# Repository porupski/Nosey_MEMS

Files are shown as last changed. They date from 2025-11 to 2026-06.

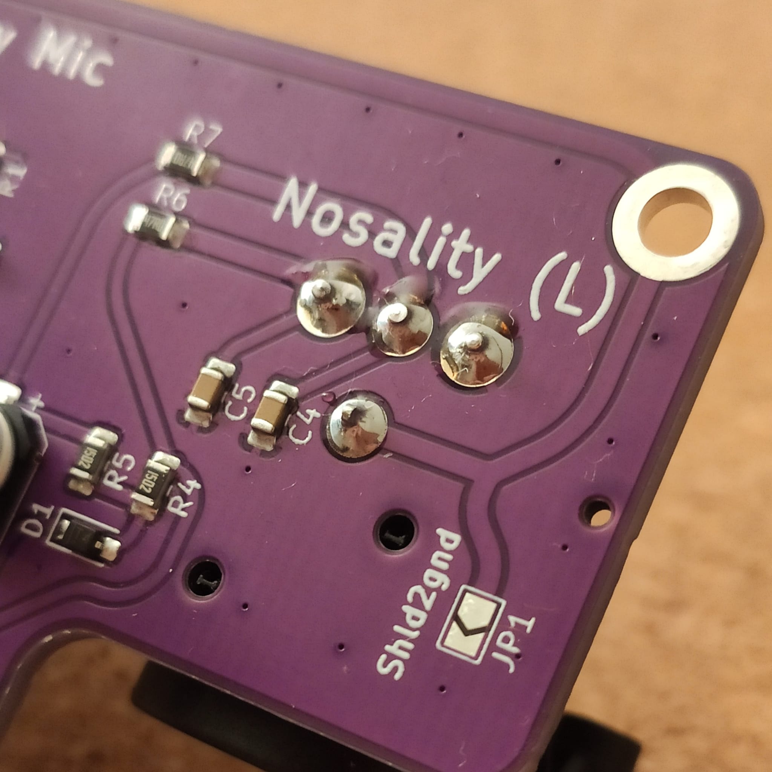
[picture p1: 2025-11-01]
docs/img/Nosey_MEMS_soldering_2.jpeg

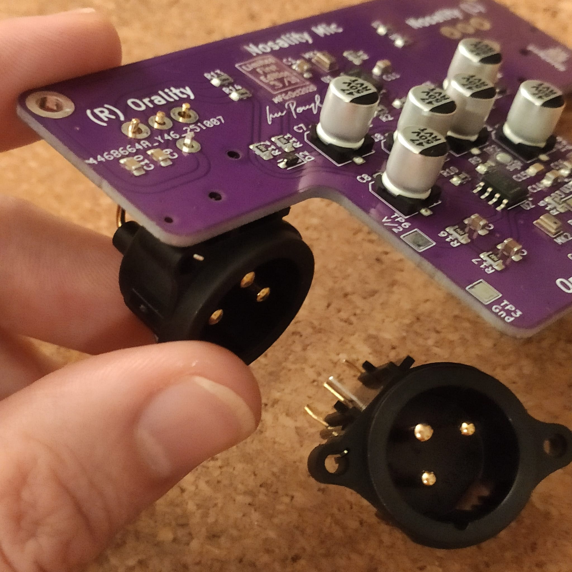
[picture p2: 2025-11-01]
docs/img/Nosey_MEMS_soldering_1.jpeg

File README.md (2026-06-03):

# Nosey MEMS

**/ˈnɔɪzi miːmz/** — a fully open-source nasometer.

Nosey MEMS is a general purpose **mono MEMS microphone preamp**. It was specifically designed for integration with **Nosey** ([GitHub](https://github.com/phoneticslab/nosey) [Paper, IS25](https://www.isca-archive.org/interspeech_2025/dewhurst25_interspeech.pdf)) for acoustic nasalance measurements. A **stereo pair of boards** — one nasal, one oral — in the (not yet) adapted Nosey 3D-printed handle and baffle.

## What you get

- Open **KiCad 10.0** schematic, PCB and JLCPCB production files
- Small 25 × 50 mm board: NA-FFA381-A10-1 MEMS mic, OPA1652 balanced output, +48V phantom via XLR3
- Simple, low-cost (~€20 per built board as of June 2026), low-maintenance design
- Built for general purpose, aimed at phonetics, but the schematic/PCB can be adapted to any use

## Where to look

- **Documentation:** [porupski.github.io/Nosey_MEMS](https://porupski.github.io/Nosey_MEMS/)
- **`KiCad_files/`** — schematic, PCB layout, production `.zip`
- **`REW_files/`** — measured frequency response (Mk1 measurements, but the circuity is basically identical)
- **`docs/legacy_mk1/`** — the first, stereo Mk1 design (superseded)

## Status

In active development. The mono Mk2 replaces the earlier single-board stereo prototype, whose shared layout compromised acoustic separation between the nasal and oral channels.

## References

- Dewhurst et al. (2025). *Nosey: Open-source hardware for acoustic nasalance.* [arXiv:2505.23339](https://arxiv.org/pdf/2505.23339) · [IS25 PDF](https://www.isca-archive.org/interspeech_2025/dewhurst25_interspeech.pdf)

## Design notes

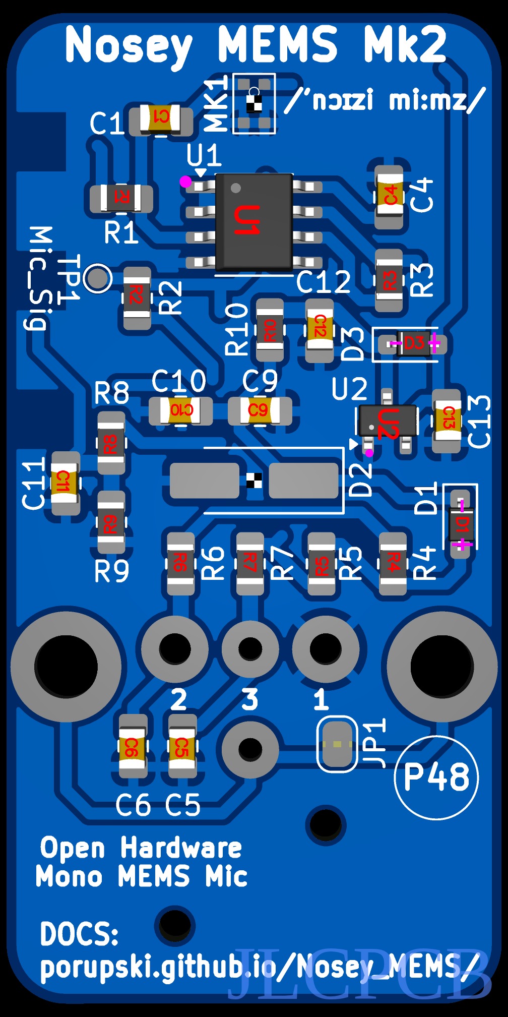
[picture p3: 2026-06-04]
docs/img/fab_Nosey_MEMS_Mk2_PCBA_placement_1.png

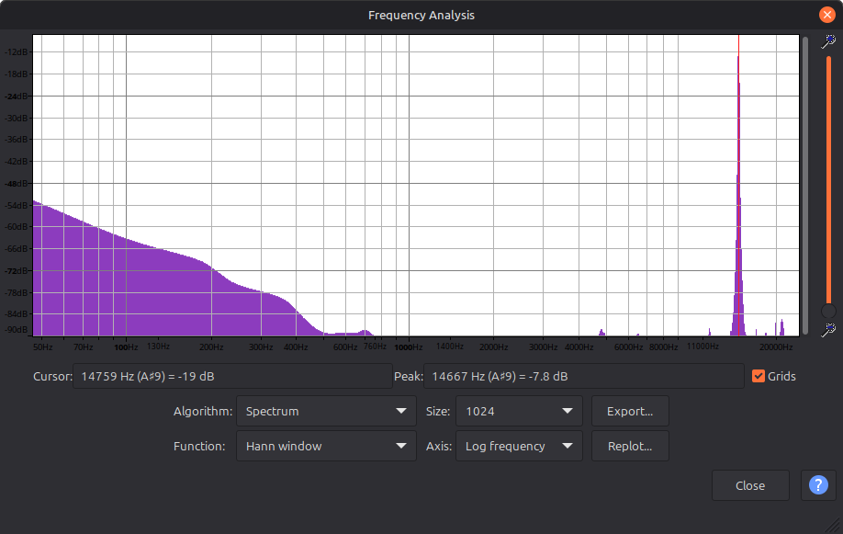
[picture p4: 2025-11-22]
docs/img/audio_plots/NoseyMEMS-R-self-resonance.png

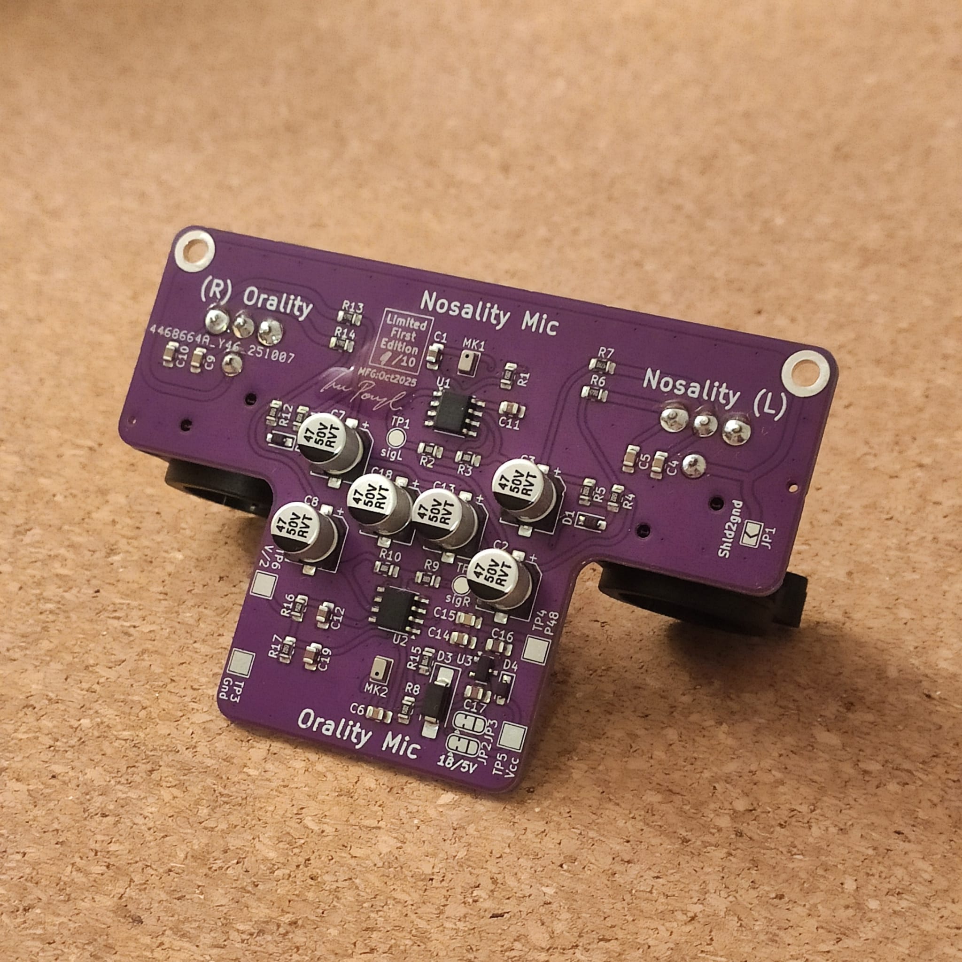
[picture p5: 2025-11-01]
docs/img/Nosey_MEMS_hero-shot_front.jpeg

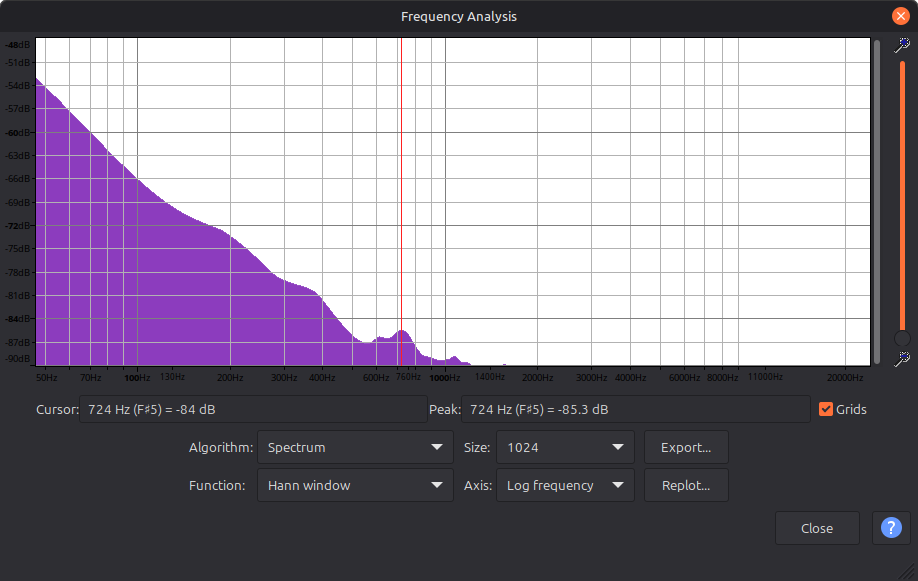
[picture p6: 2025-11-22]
docs/img/audio_plots/NoseyMEMS-R-noise.png

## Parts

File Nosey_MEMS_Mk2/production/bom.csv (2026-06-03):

Designator | Footprint | Quantity | Value | LCSC Part #
C1, C4, C9 | 0805 | 3 | 2.2uF
C10 | 0805 | 1 | 10nF
C11, C12, C13 | 0805 | 3 | 10uF
C2, C3, C7, C8 | CP_Elec_6.3x7.7 | 4 | 47uF
C5, C6 | 0805 | 2 | 22nF
D1, D3 | D_SOD-323_HandSoldering | 2 | 1N4148
D2 | D_SMA_Handsoldering | 1 | 1SMA4746A
MK1 | NA-FFA381-A10-1_MEMS_mic_analog_v1 | 1 | NA-FFA381-A10-1
R1, R4, R5, R8, R9 | 0805 | 5 | 15k
R10 | 0805 | 1 | 470R
R2, R3 | 0805 | 2 | 3k
R6, R7 | 0805 | 2 | 47R
U1 | SOIC-8_3.9x4.9mm_P1.27mm | 1 | OPA1652
U2 | SOT-23 | 1 | PJ71K30SC

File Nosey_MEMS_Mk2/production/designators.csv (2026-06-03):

C1:1
C10:1
C11:1
C12:1
C13:1
C2:1
C3:1
C4:1
C5:1
C6:1
C7:1
C8:1
C9:1
D1:1
D2:1
D3:1
H1:1
H2:1
J1:1
JP1:1
JP2:1
JP3:1
MK1:1
R1:1
R10:1
R2:1
R3:1
R4:1
R5:1
R6:1
R7:1
R8:1
R9:1
TP1:1
TP2:1
TP3:1
TP4:1
TP5:1
U1:1
U2:1

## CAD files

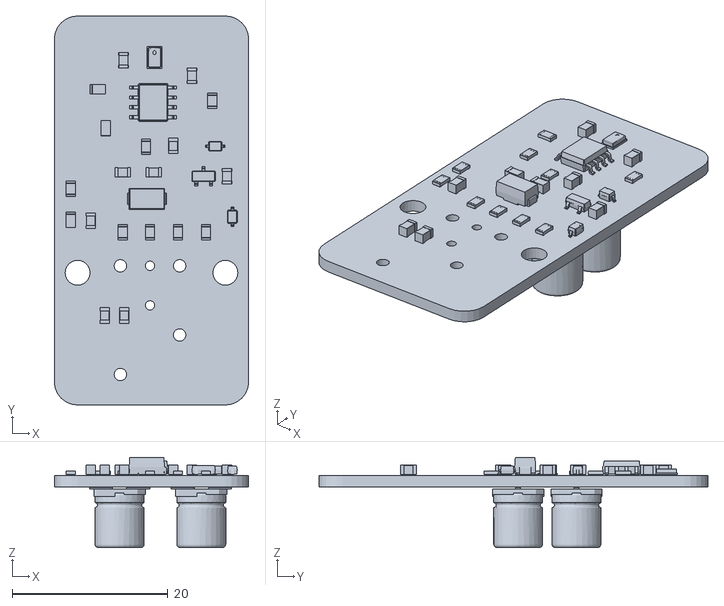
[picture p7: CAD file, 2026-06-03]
Nosey_MEMS_Mk2/Nosey_MEMS_Mk2_PCB_model_iv2.1.stl
25.0 x 50.0 x 11.6

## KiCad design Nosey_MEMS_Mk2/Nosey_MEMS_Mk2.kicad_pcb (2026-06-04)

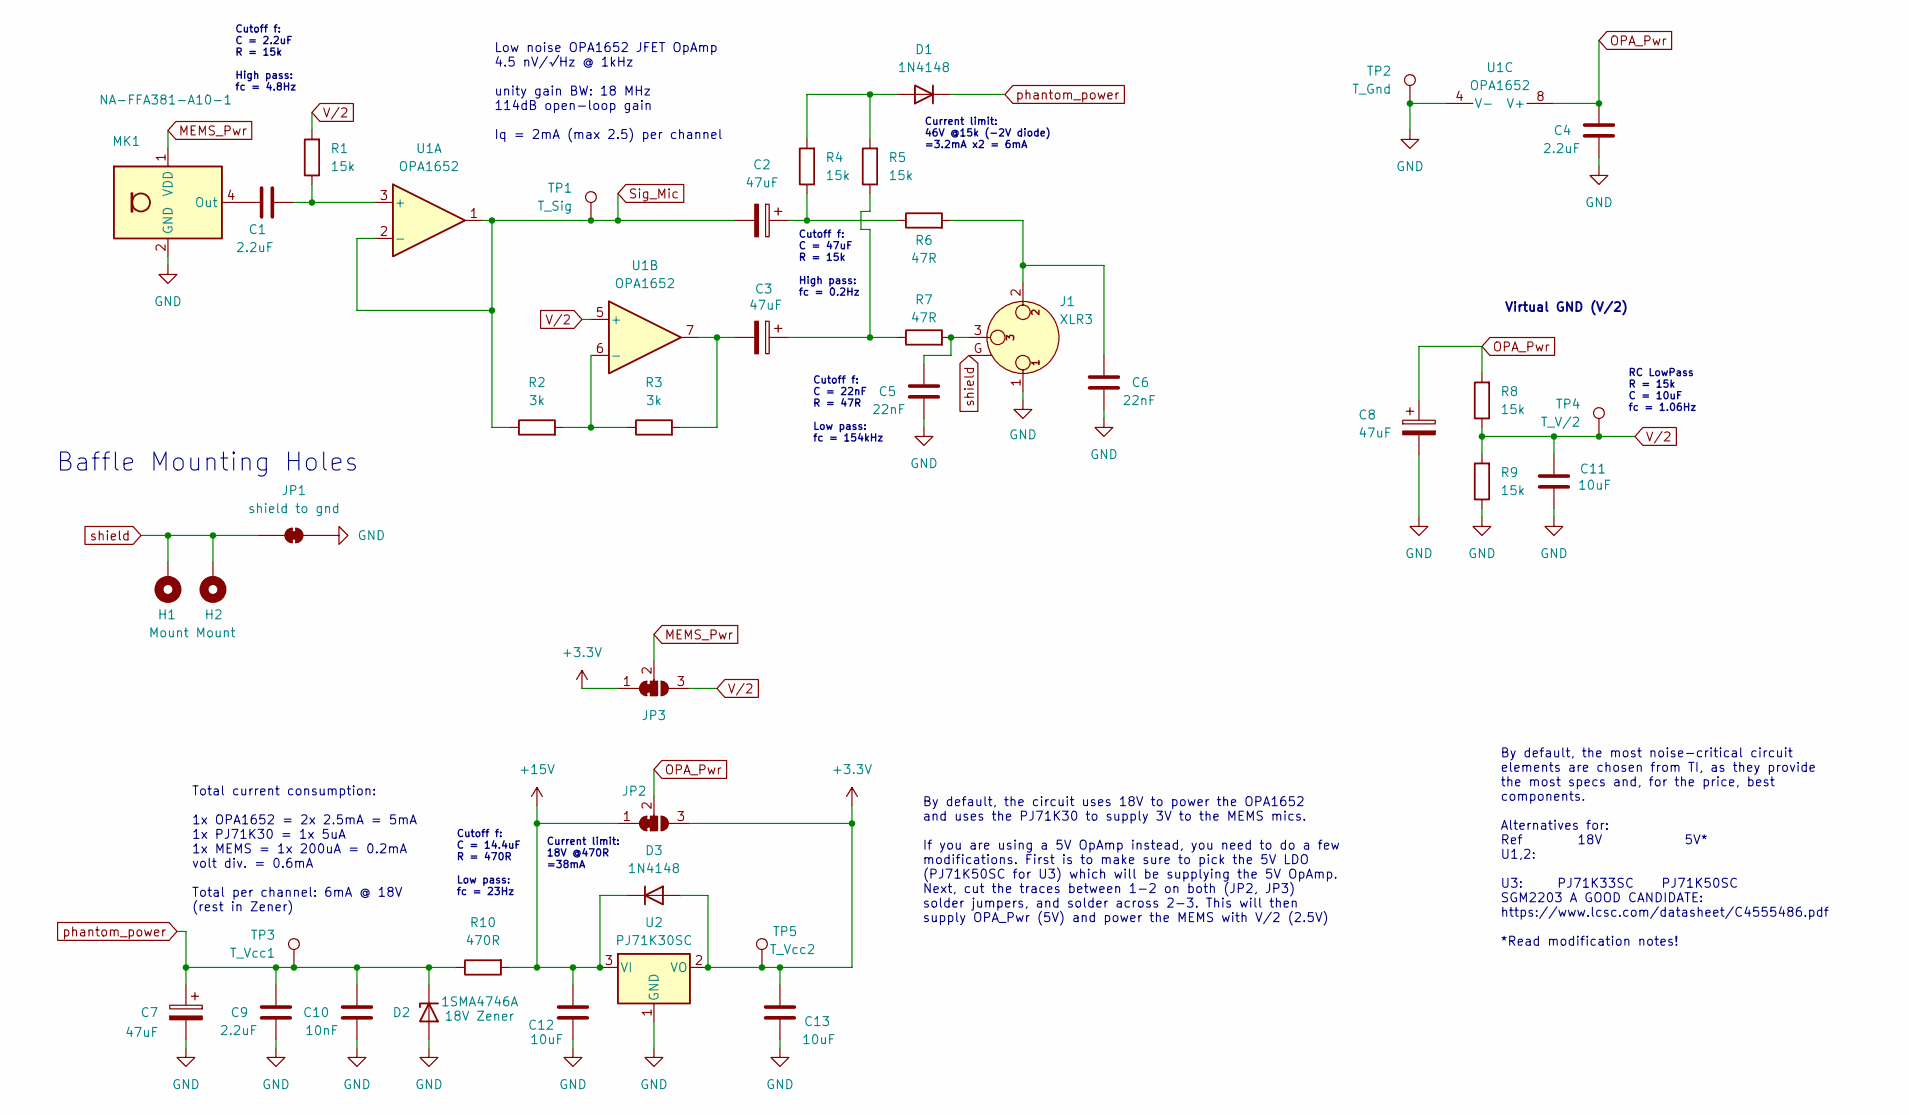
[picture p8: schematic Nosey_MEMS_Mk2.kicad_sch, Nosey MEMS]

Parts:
C1, C4, C9: 2.2uF; C_0805_2012Metric_Pad1.18x1.45mm_HandSolder
C2, C3, C7, C8: 47uF; CP_Elec_6.3x7.7
C5, C6: 22nF; C_0805_2012Metric_Pad1.18x1.45mm_HandSolder
C10: 10nF; C_0805_2012Metric_Pad1.18x1.45mm_HandSolder
C11, C12, C13: 10uF; C_0805_2012Metric_Pad1.18x1.45mm_HandSolder
D1, D3: 1N4148; D_SOD-323_HandSoldering
D2: 1SMA4746A; D_SMA_Handsoldering
H1, H2: Mount; MountingHole_3.2mm_M3_DIN965_Pad
J1: XLR3; Jack_XLR_Neutrik_NC3MAAH_Horizontal
JP1: shield to gnd; SolderJumper-2_P1.3mm_Bridged2Bar_RoundedPad1.0x1.5mm
JP2, JP3: SolderJumper_3_Open; SolderJumper-3_P1.3mm_Bridged12_RoundedPad1.0x1.5mm
MK1: NA-FFA381-A10-1; NA-FFA381-A10-1_MEMS_mic_analog_v1
R1, R4, R5, R8, R9: 15k; R_0805_2012Metric_Pad1.20x1.40mm_HandSolder
R2, R3: 3k; R_0805_2012Metric_Pad1.20x1.40mm_HandSolder
R6, R7: 47R; R_0805_2012Metric_Pad1.20x1.40mm_HandSolder
R10: 470R; R_0805_2012Metric_Pad1.20x1.40mm_HandSolder
TP1: T_Sig; TestPoint_Pad_D1.0mm
TP2: T_Gnd; TestPoint_Pad_2.5x2.5mm
TP3: T_Vcc1; TestPoint_Pad_2.5x2.5mm
TP4: T_V/2; TestPoint_Pad_2.5x2.5mm
TP5: T_Vcc2; TestPoint_Pad_2.5x2.5mm
U1: OPA1652; SOIC-8_3.9x4.9mm_P1.27mm
U2: PJ71K30SC; SOT-23

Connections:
+3.3V: C13.1, D3.2 (A), JP2.3 (B), JP3.1 (A), TP5.1 (1_1), U2.2 (VO)
+15V: C12.1, D3.1 (K), JP2.1 (A), R10.2, U2.3 (VI)
GND: C4.2, C5.2, C6.2, C7.2, C8.2, C9.2, C10.2, C11.2, C12.2, C13.2, D2.2 (A), J1.1, JP1.2 (B), MK1.2 (GND), MK1.3 (GND), R9.1, TP2.1 (1_1), U1.4 (V-), U2.1 (GND)
MEMS_Pwr: JP3.2 (C), MK1.1 (VDD)
unnamed: C2.1, R4.1, R6.1
unnamed: C3.1, R5.1, R7.1
unnamed: C3.2, R3.2, U1.7
unnamed: C5.1, J1.3, R7.2
unnamed: C6.1, J1.2, R6.2
unnamed: D1.2 (A), R4.2, R5.2
unnamed: C1.1, MK1.4 (Out)
unnamed: C1.2, R1.1, U1.3 (+)
unnamed: R2.2, R3.1, U1.6 (-)
OPA_Pwr: C4.1, C8.1, JP2.2 (C), R8.2, U1.8 (V+)
Sig_Mic: C2.2, R2.1, TP1.1 (1_1), U1.1, U1.2 (-)
V/2: C11.1, JP3.3 (B), R1.2, R8.1, R9.2, TP4.1 (1_1), U1.5 (+)
phantom_power: C7.1, C9.1, C10.1, D1.1 (K), D2.1 (K), R10.1, TP3.1 (1_1)
shield: H1.1 (1_1), H2.1 (1_1), J1.G, JP1.1 (A)

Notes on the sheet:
Current limit: 46V @15k (-2V diode) =3.2mA x2 = 6mA
RC LowPass R = 15k C = 10uF fc = 1.06Hz
Virtual GND (V/2)
Current limit: 18V @470R =38mA
Cutoff f: C = 2.2uF R = 15k High pass: fc = 4.8Hz
By default, the most noise-critical circuit elements are chosen from TI, as they provide the most specs and, for the price, best components. Alternatives for: Ref 18V 5V* U1,2: U3: PJ71K33SC PJ71K50SC SGM2203 A GOOD CANDIDATE: https://www.lcsc.com/datasheet/C4555486.pdf *Read modification notes!
Cutoff f: C = 22nF R = 47R Low pass: fc = 154kHz
By default, the circuit uses 18V to power the OPA1652 and uses the PJ71K30 to supply 3V to the MEMS mics. If you are using a 5V OpAmp instead, you need to do a few modifications. First is to make sure to pick the 5V LDO (PJ71K50SC for U3) which will be supplying the 5V OpAmp. Next, cut the traces b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
Total current consumption: 1x OPA1652 = 2x 2.5mA = 5mA 1x PJ71K30 = 1x 5uA 1x MEMS = 1x 200uA = 0.2mA volt div. = 0.6mA Total per channel: 6mA @ 18V (rest in Zener)
Cutoff f: C = 14.4uF R = 470R Low pass: fc = 23Hz
Baffle Mounting Holes
Cutoff f: C = 47uF R = 15k High pass: fc = 0.2Hz
Low noise OPA1652 JFET OpAmp 4.5 nV/√Hz @ 1kHz unity gain BW: 18 MHz 114dB open-loop gain Iq = 2mA (max 2.5) per channel

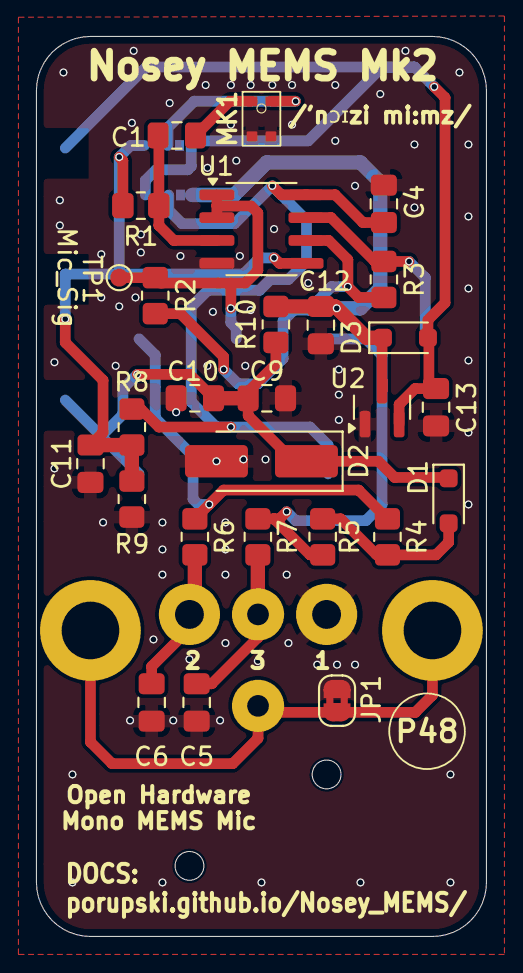
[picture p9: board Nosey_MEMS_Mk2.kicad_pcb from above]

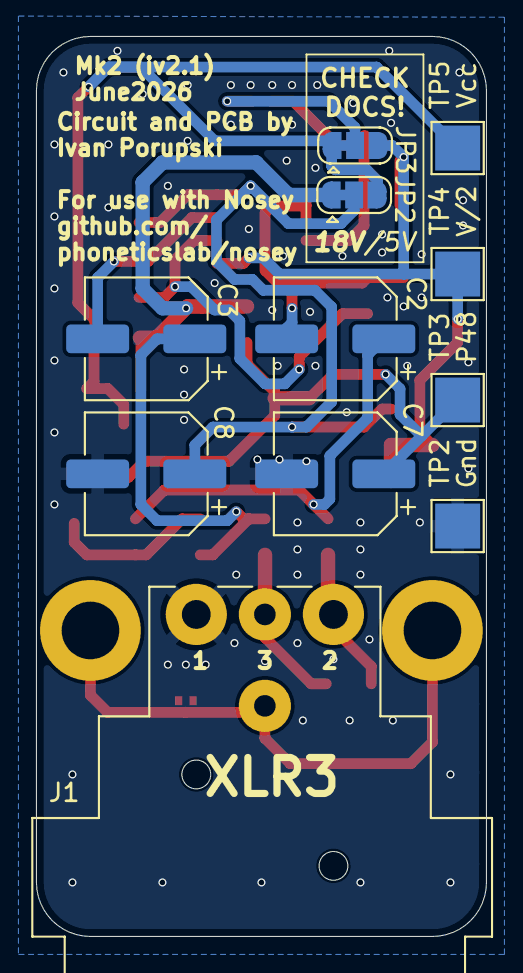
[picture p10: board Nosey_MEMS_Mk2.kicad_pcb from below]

Board: 2 copper layers, 25.0 x 50.0 mm, 40 parts (11 on the bottom side), 18 nets.

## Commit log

2025-10-05 Added the manufacture.html subpage with assembly information. Minor style and typo edits.
2025-10-06 Massive update to Manufacturing Guide. Finer details in index and style, added calibration.html starter page.
2025-10-07 Added debug prints to .js
2025-10-08 Updated PCB image v2
2025-11-01 Expanded on Manufacturing with newly received Nosey MEMS. Did the Calibration test and documented the steps and results.
2025-11-01 Added first public versions of the KiCad9 schematic and pcb board. Added first preliminary REW frequency sweep on both mics.
2025-11-01 Added hero shots of the finished device, front and back. Minor text editing.
2025-11-22 Added to Calibration some Noise floor and Resonance responses. Included a stereo /ama/ /ana/ .wav file recorded with Nosey MEMS for first nasalance testing in practice.
2026-06-03 Added first schematic and pcb for Mk2! Includes JLCPCB production files and STL model.
    [Nosey_MEMS_Mk2.kicad_pcb, Nosey_MEMS_Mk2.kicad_sch, Nosey_MEMS_Mk2_PCB_model_iv2.1.stl, bom.csv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]
2026-06-03 TestPads causing issues for assembly ordering, better now.
    [Nosey_MEMS_Mk2.kicad_pcb, Nosey_MEMS_Mk2.kicad_sch, bom.csv]
2026-06-04 BIG UPDATE: Presenting Nosey MEMS Mk2! General purpose mono MEMS microphone + preamp, with nasometry in mind. More to come soon.
    [Nosey_MEMS_Mk2.kicad_pcb]
